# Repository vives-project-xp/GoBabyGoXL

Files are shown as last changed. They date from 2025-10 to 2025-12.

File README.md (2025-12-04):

# GOBABYGOXL (Dit is een prototype)
## Team
- [Maarten Audenaert](https://github.com/MaartenAudenaert)
- [Mauro Carlier](https://github.com/maurocarlier)
- [Danae Zutterman](https://github.com/Danaezutterman)
- [Robbe Lambrechts](https://github.com/lomopoio)
- [Thomas Demeulenaere](https://github.com/Thomas8650)
- [Jarno Bostyn](https://github.com/Jarno-max)

## De opdracht
De bedoeling is om verder te werken op het GoBabyGo-project van de vorige jaren. De doelstelling van dit project is om kinderen 
met een motorische beperking toch zelfstandig te kunnen laten voortbewegen. Dit wordt gedaan door middel van een auto waarvan 
we het gaspedaal vervangen door een knop op het stuur. De GoBabyGo was voor iets kleinere kinderen en nu is het de bedoeling dat we een 
XL-versie maken voor kinderen die te groot zijn geworden voor de vorige auto.

## Affiches

<div style="display: flex; gap: 10px;">
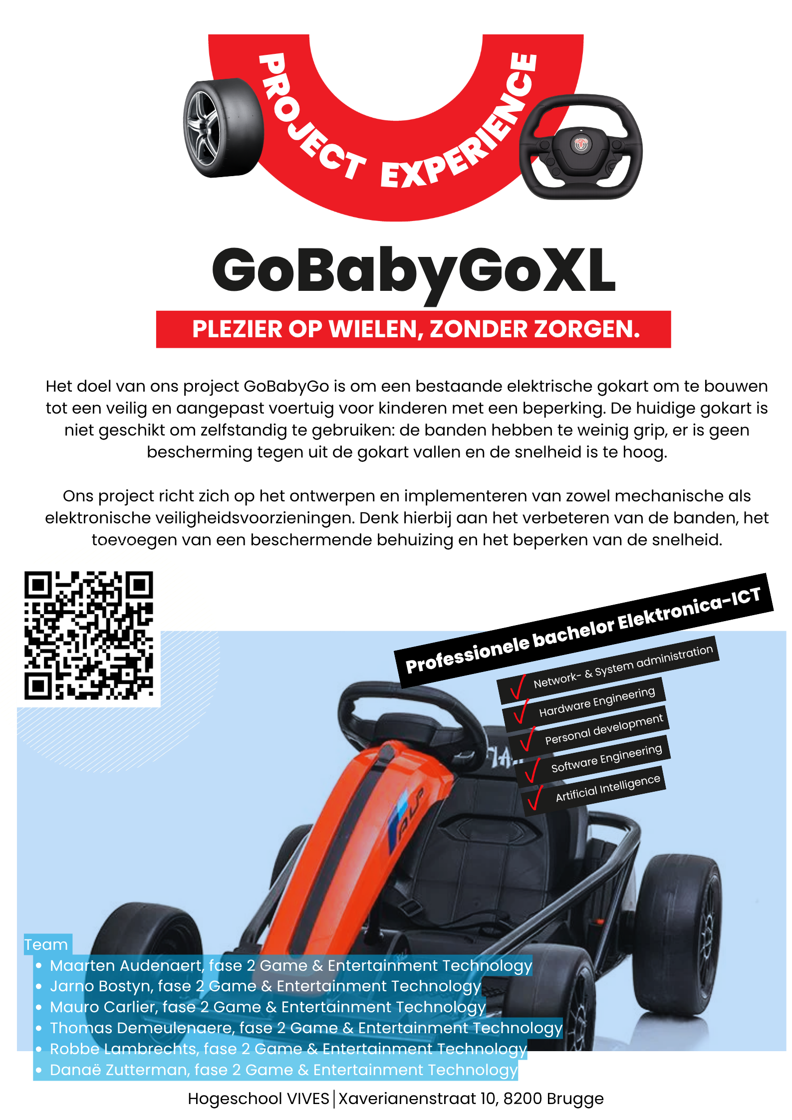
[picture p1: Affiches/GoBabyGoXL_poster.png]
   
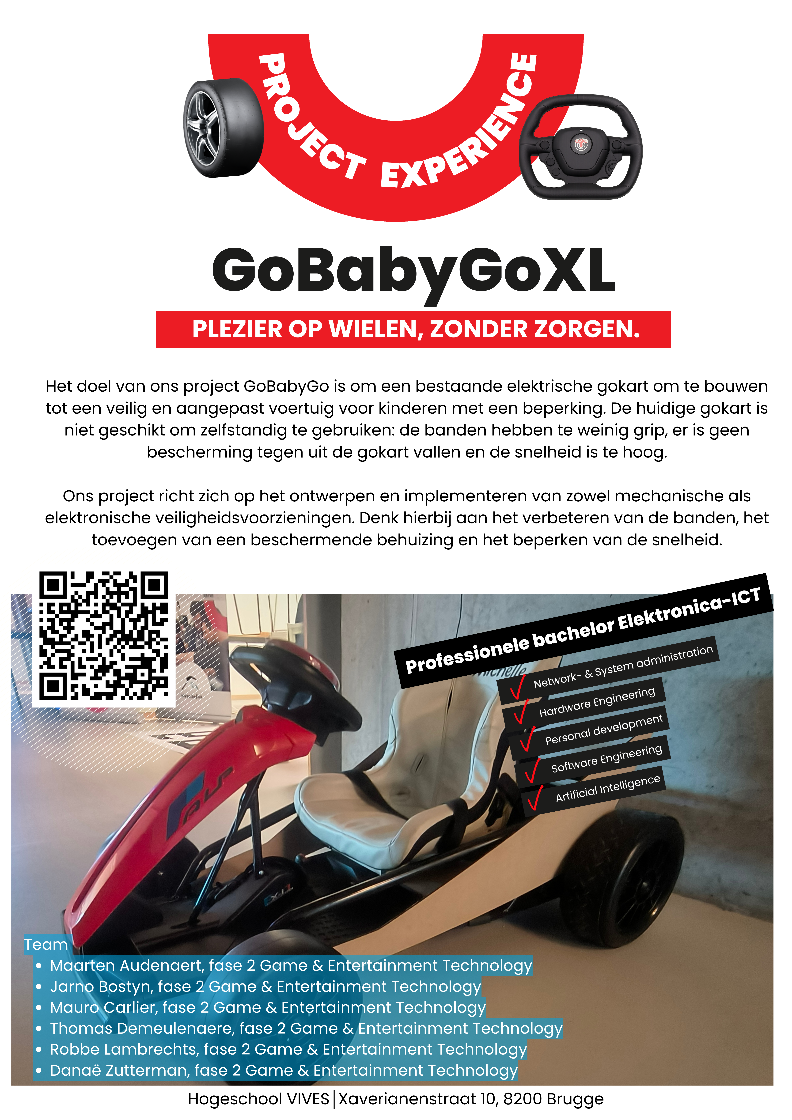
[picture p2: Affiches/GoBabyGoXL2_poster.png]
   
</div>

## Folder structuur
- [3d-prints](./3d-prints/readme.md) : Hier bevindt alles om de onderdelen te 3D-printen.
- [Affiches](./Affiches/GoBabyGoXL_poster.png ) : Hier vindt u onze poster.
- [Archief](./Archief/README.md) : Hier vindt u al onze research.
- [Gaspedaal naar knop](./Gaspedaal%20naar%20knop/README.md) : Hier bevindt alles van hoe we het  gaspedaal hebben vervangen door een knop. 
- [Grip banden](./Grip%20banden/README.md) : Hier bevindt alles hoe we de grip van de banden verbeteren.
- [Handleidingen](./Handleidingen/readme.md) : Hier vindt u de handleidingen voor het aanpassen van de auto.
- [Inriching auto](<Inrichting auto/README.md>) : Hier bevindt alles hoe we de auto veilig maken voor het kind.
- [Instagram post](./Instagram%20Post/Readme.md) : Hier vindt u onze instagram post.
- [Joystick](./Joystick/readme.md) : Hier wordt er nagedacht over de uitbreiding met een joystick.
- [Lasercutten](./Lasercutten/readme.md) : Hier bevindt alles om de onderdelen te lasercutten.

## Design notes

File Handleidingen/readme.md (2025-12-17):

# Handleiding om de auto om te bouwen
### Let op: dit is een prototype!

[**Benodigdheden om de auto om te bouwen**](#Benodigdheden)

[**Gereedschapsbenodigdheden**](#Gereedschap)

[**Handleiding om de auto om te bouwen met de knop**](#Handleiding-om-auto-om-te-bouwen-met-knop)

[**Handleiding om de auto om te bouwen met de joystick**](#Handleiding-om-auto-om-te-bouwen-met-joystick)

[**Kostprijs per auto**](#Kostprijs-per-auto)

---

## Benodigdheden 
Hier vindt u alle benodigdheden om 1 auto om te bouwen.

[**Benodigdheden knop**](#Knop)

[**Benodigdheden joystick**](#Joystick)

---
## Kostprijs per auto
[**Kostprijs**](https://github.com/vives-project-xp/GoBabyGoXL/tree/main/Handleidingen/KostprijsPerAuto)

---

### Knop

1x: [Knop Ergo](https://www.kmd.nl/producten/overige-hulpmiddelen/schakelaars/big-red)

2x: [Seconden Epoxylijm](https://www.hubo.be/nl/p/pattex-super-mix-universal-mini-epoxy-colle-bi-composant-6ml/249565/#specs)

4x: [Buizenklem 32mm](https://www.hubo.be/nl/p/astore-buisklem-32mm-polypropyleen/890700/)

6x: [Buizenklem 25mm](https://www.hubo.be/nl/p/buisklem-pp-25mm/972187/)

2x: [Buizenklem 20mm](https://www.hubo.be/nl/p/scala-buisklem-20mm-polypropyleen/994224/)

2x: [Rubber](https://www.hubo.be/nl/p/rubbermat-op-rol-traanplaat-1-5m-per-lopende-meter/131516/) (l= 86,8cm ; b=8cm)

12x: [Bouten M6 20mm](https://www.hubo.be/nl/p/mack-binnenzeskantbout-m6-20mm-verzinkt-7-stuks/208802/)

12x: [Zeskantdopmoer M6](https://www.hubo.be/nl/p/pgb-fasteners-zeskantdopmoer-din1587-m6-zwart-12-stuks/1057451/) 

1x: [Grondplaat voor stoel](https://github.com/vives-project-xp/GoBabyGoXL/tree/main/Lasercutten/Grondplaat) (lasercut)

1x: [Verhoogstuk voor stoel](https://github.com/vives-project-xp/GoBabyGoXL/blob/main/3d-prints/Helling%20stoeltje/HellingPX1%20v2.stl) (3D-print)

1x: [Velcro voor stoel](https://jbsigns.be/product/klittenband/)

1x: [Vervanging gaspedaal](https://github.com/vives-project-xp/GoBabyGoXL/blob/main/3d-prints/Gaspedaal%20plaatje/Gaspedaalv3.stl) (3D-print)

1x: [Vervanging HIGH SPEED LOW SPEED knop](https://github.com/vives-project-xp/GoBabyGoXL/blob/main/3d-prints/Dekseltje%20voor%20knop%20en%20hendel/dekseltje_sloped%20v2.stl) (3D-print)

2x: [Zijkant houten platen](https://github.com/vives-project-xp/GoBabyGoXL/tree/main/Lasercutten/Zijkant%20platen) (lasercut)

2x: [Wrapping voor zijplaten](https://www.hubo.be/nl/p/zelfklevende-folie-45cm-x-2m-mat-zwart/367781/)

1x: [Kill switch](https://rosso-parts.com/products/high-low-speed-switch)

---

### Joystick

1x: [Joystick](https://www.conrad.be/nl/p/joy-it-arcade-joystick-professional-8-invoerapparaat-geschikt-voor-arduino-banana-pi-cubieboard-pcduino-raspberry-pi-1555268.html?cq_src=google_ads&cq_cmp=21348122838&cq_term=&cq_plac=&cq_net=x&cq_plt=gp&utm_source=google&utm_medium=cpc&utm_campaign=BE+-+PMAX+-+Nonbrand+-+Zero+traffic&utm_id=21348122838&gad_source=1&gad_campaignid=21354377450&gbraid=0AAAAAD8JkRqEt0kc6sfABQWvpGkQomOKD&gclid=CjwKCAjwup3HBhAAEiwA7euZuuzKnT1HKtYVqYWcoFUZA91DAXJudML3s6RHekIYH-F_8EoZS52qvxoC-UwQAvD_BwE&refresh=true)

1x: [DC-motor](https://www.tinytronics.nl/nl/mechanica-en-actuatoren/motoren/dc-motoren/aslong-pg42-775-transmissiemotor-24v-dc-90rpm)

1x: [Dc-converter 24V --> 12V](https://www.reichelt.com/be/nl/shop/product/dc_dc-converter_12_7_v_5_a-300230?PROVID=2812)

1x: [ESP32](https://www.tinytronics.nl/nl/development-boards/microcontroller-boards/met-wi-fi/lilygo-ttgo-t-display-v1.1-esp32-met-1.14-inch-tft-display)

1x  [24V->5v USB converter module](https://www.amazon.nl/gp/product/B07JLTTZXL?smid=A3U3NV7MT8POQS&psc=1)

1x: [Driver H-brug](https://www.otronic.nl/nl/l298n-motor-driver-board-rood.html?source=googlebase&gad_source=1&gad_campaignid=19639985996&gbraid=0AAAAACZK5qu8Z-8RFgjMXGjDdSz0dZhw3&gclid=CjwKCAiA_dDIBhB6EiwAvzc1cA0ZIi9ejuDw5lKT-S1ZbPfsZyDSasSXt8XzMPAZVOmllBPeCYmQxhoCnuUQAvD_BwE)

2x: [Seconden Epoxylijm](https://www.hubo.be/nl/p/pattex-super-mix-universal-mini-epoxy-colle-bi-composant-6ml/249565/#specs)

4x: [Buizenklem 32mm](https://www.hubo.be/nl/p/astore-buisklem-32mm-polypropyleen/890700/)

6x: [Buizenklem 25mm](https://www.hubo.be/nl/p/buisklem-pp-25mm/972187/)

2x: [Buizenklem 20mm](https://www.hubo.be/nl/p/scala-buisklem-20mm-polypropyleen/994224/)

2x: [Rubber](https://www.hubo.be/nl/p/rubbermat-op-rol-traanplaat-1-5m-per-lopende-meter/131516/) (l= 86,8cm ; b=8cm)

12x: [Bouten M6 20mm](https://www.hubo.be/nl/p/mack-binnenzeskantbout-m6-20mm-verzinkt-7-stuks/208802/)

12x: [Zeskantdopmoer M6](https://www.hubo.be/nl/p/pgb-fasteners-zeskantdopmoer-din1587-m6-zwart-12-stuks/1057451/)

1x: [Grondplaat voor stoel](https://github.com/vives-project-xp/GoBabyGoXL/tree/main/Lasercutten/Grondplaat) (lasercut)

1x: [Verhoogstuk voor stoel](https://github.com/vives-project-xp/GoBabyGoXL/blob/main/3d-prints/Helling%20stoeltje/HellingPX1%20v2.stl) (3D-print)

1x: [Velcro voor stoel](https://jbsigns.be/product/klittenband/)

1x: [Vervanging gaspedaal](https://github.com/vives-project-xp/GoBabyGoXL/blob/main/3d-prints/Gaspedaal%20plaatje/Gaspedaalv3.stl) (3D-print)

1x: [Vervanging HIGH SPEED LOW SPEED knop + Voorwaarts/achterwaarts knop](https://github.com/vives-project-xp/GoBabyGoXL/blob/main/3d-prints/Dekseltje%20voor%20knop%20en%20hendel/deksel_combo.stl) (3D-print)

1x: [DC-motor houder](https://github.com/vives-project-xp/GoBabyGoXL/tree/main/3d-prints/DC-voeding%20houder) (3d-print)

1x: [Assenkoppeling](https://www.motedis.be/nl/Assen-Koppelingen-flexibel-Mot-D25L30-8-12mm)

2x: [Zijkant houten platen](https://github.com/vives-project-xp/GoBabyGoXL/tree/main/Lasercutten/Zijkant%20platen) (lasercut)

2x: [Wrapping voor zijplaten](https://www.hubo.be/nl/p/zelfklevende-folie-45cm-x-2m-mat-zwart/367781/)

1x: [Kill switch](https://rosso-parts.com/products/high-low-speed-switch)

---

## Gereedschap
- 3D printer
- Lasercutter
- Setje schroevendraaiers
- Boormachine
- Soldeerbout + accessoires
- Kniptang + universele tang
- Usb-c kabel
- Setje dopsleutels
- Dremel
- Houtlijm            
- Breekmes
- Schuifmaat/Meter
- Multimeter
- Slijpschijf
- Koperdraad/Jumper wires
- Krimpkous
- Pattex spraylijm
- Twee M4 25mm bouten
- Twee M4 50mm bouten
- Heatgun

---

## Handleiding om auto om te bouwen met knop

[**Installatie van de knop**](#Knop-installeren)

[**Bevestiging van de knop**](#Bevestiging-van-de-knop)

[**Bevestigingsplaatje voor het gaspedaal**](#Bevestigen-plaatje-van-gaspedaal)

[**Begrenzen van de snelheid**](#Snelheidsbegrenzing)

[**Bevestigensplaatje voor de High- en Low speed knop**](#Bevestigen-plaatje-van-high--en-low-speed-knop)

[**Montage van de grondplaat**](#Montage-Grondplaat)

[**Plaatsen van de stoel**](#Bevestigen-van-de-stoel)

[**Wrappen + monteren van de zijplaten**](#wrappen--monteren-van-de-zijplaten)

[**Grip voor de banden**](#Grip-banden)

[**Kill switch**](#Kill-switch)

---

### Knop installeren

Als eerste maak je de vier schroeven los zodat je het gaspedaaltje kan verwijderen.

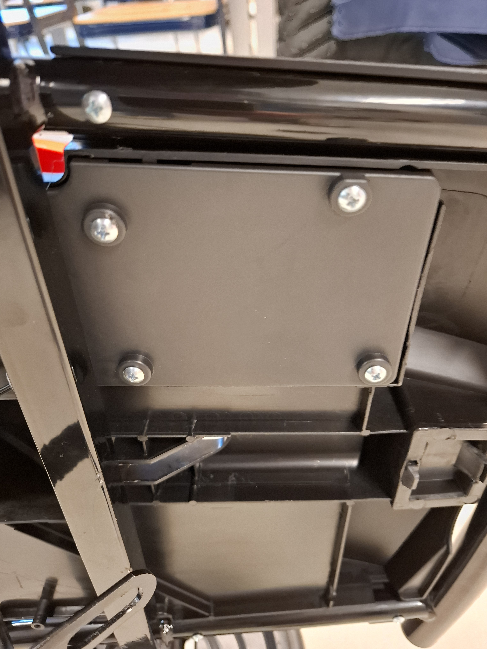
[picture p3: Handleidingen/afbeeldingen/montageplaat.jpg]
bevestigingsplaat


Het gaspedaaltje verwijder je door het met wat kracht omhoog te duwen.

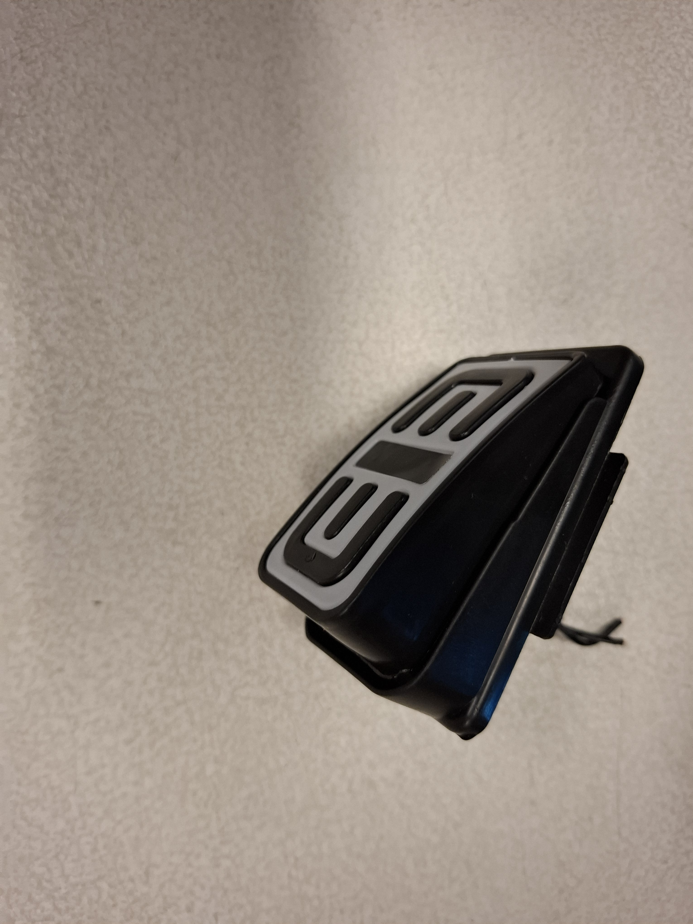
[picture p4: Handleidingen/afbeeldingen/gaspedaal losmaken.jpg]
gaspedaal


Vervolgens knip je de zwarte kabels die aan het gaspedaal vastzitten los.

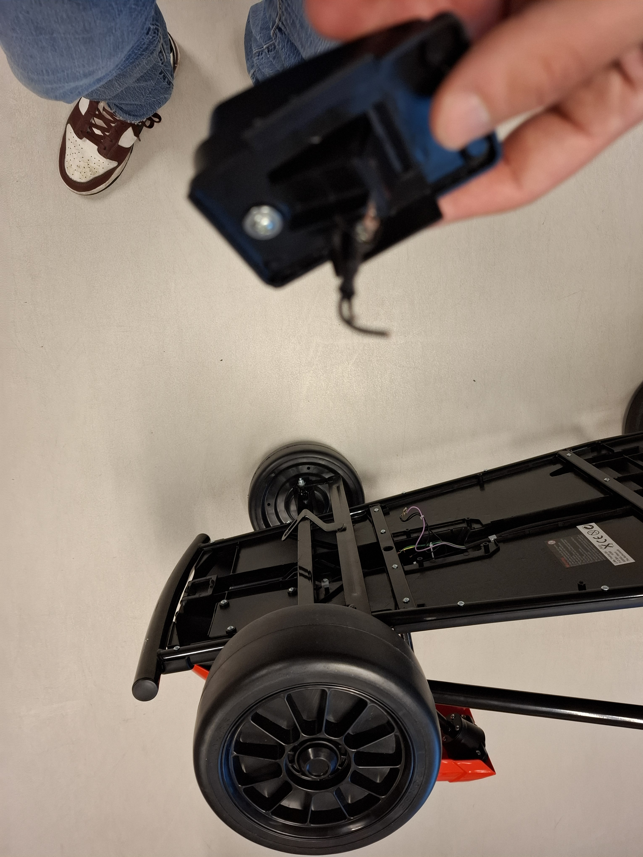
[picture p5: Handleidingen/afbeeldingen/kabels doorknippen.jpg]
kabels doorknippen


Daarna verleng je de draden van de knop en de kabels van het gaspedaal, en soldeer je deze zorgvuldig aan elkaar.

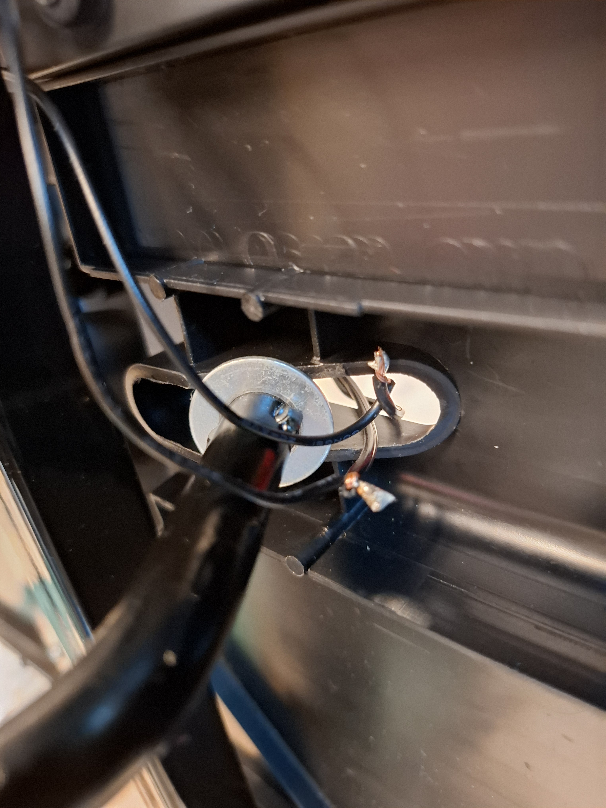
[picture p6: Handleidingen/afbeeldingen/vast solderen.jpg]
solderen


---

### Bevestiging van de knop
1) Dit is het stuur van de auto.
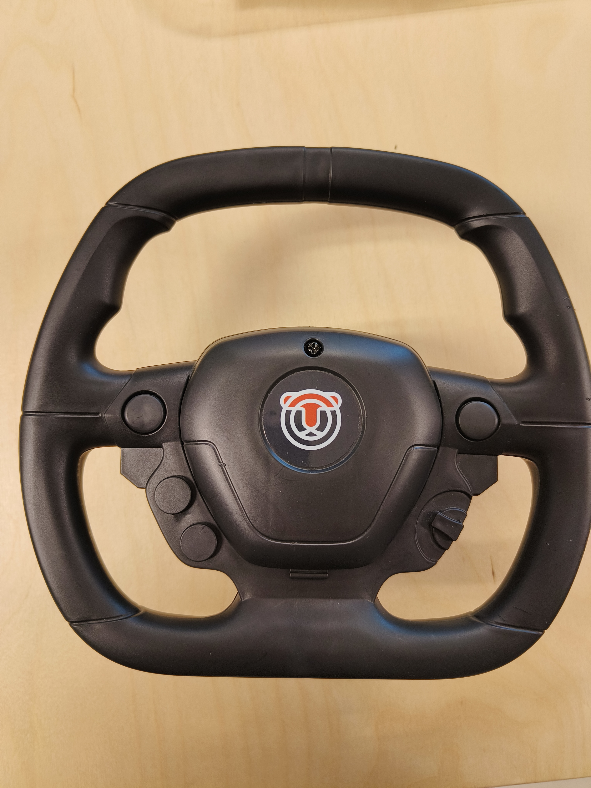
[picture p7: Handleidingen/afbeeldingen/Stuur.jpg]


2) Nu leg je de knop in het midden van het stuur, je tekent hier 1 gaatje af om de knop te bevestigen. Hierna maak je een gaatje in het stuur.
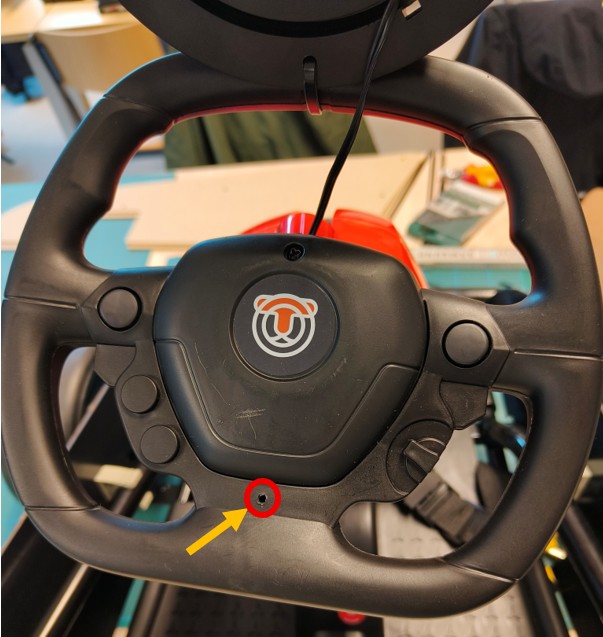
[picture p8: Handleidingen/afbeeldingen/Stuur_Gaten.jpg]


3) Nu maak je een gaatje in de knop boven en onderaan daarna plaats je de knop op het stuur, en monteer je het.
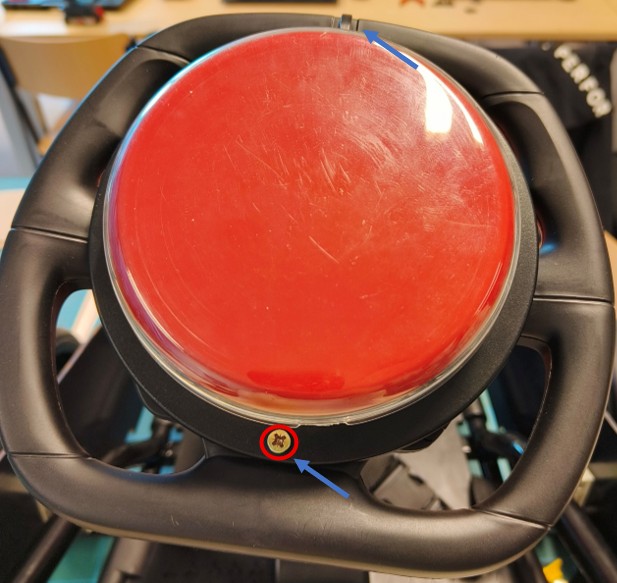
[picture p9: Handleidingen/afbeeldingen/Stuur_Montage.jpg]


---

### Bevestigen plaatje van gaspedaal
1) Eerste verwijder je het origineel gaspedaaltje.
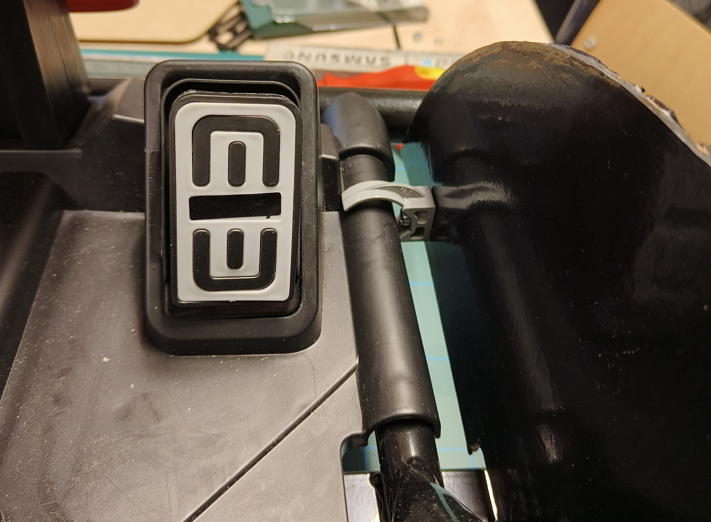
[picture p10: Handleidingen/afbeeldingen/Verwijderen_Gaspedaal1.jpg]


2) Nu heb je een lege opening.
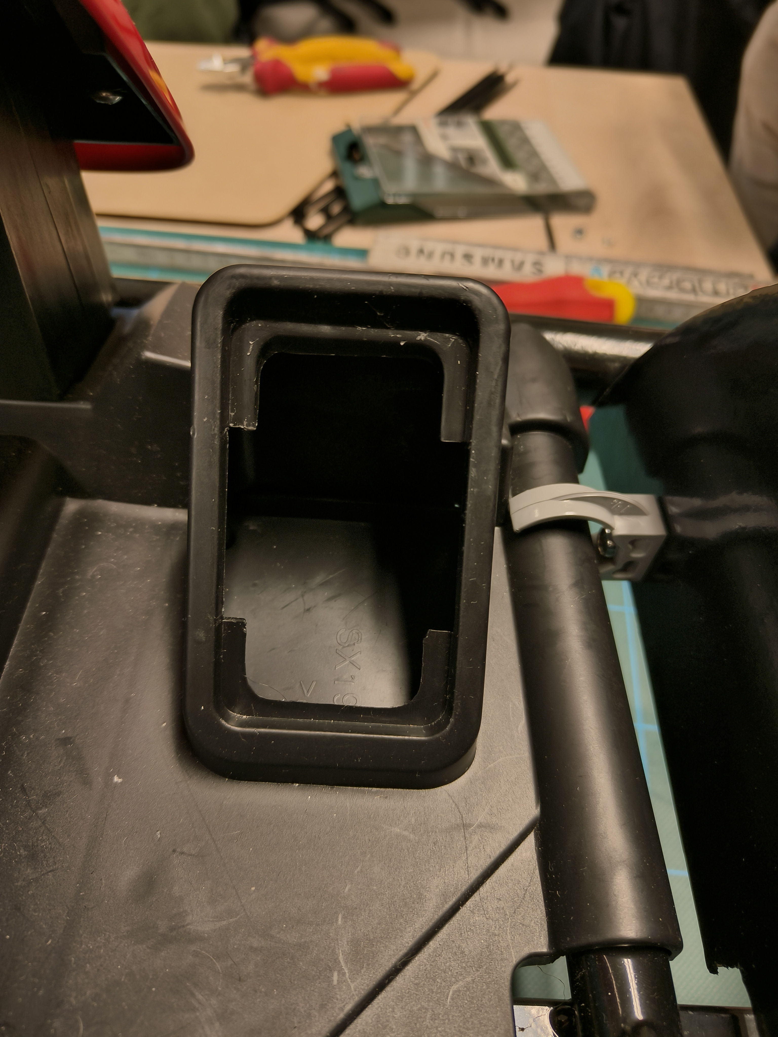
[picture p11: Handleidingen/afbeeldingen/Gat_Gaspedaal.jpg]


3) Nu plaats je het 3D geprinte gaspedaaltje, hiervoor heb je geen lijm nodig.
   
<div style="display: flex; gap: 10px;">
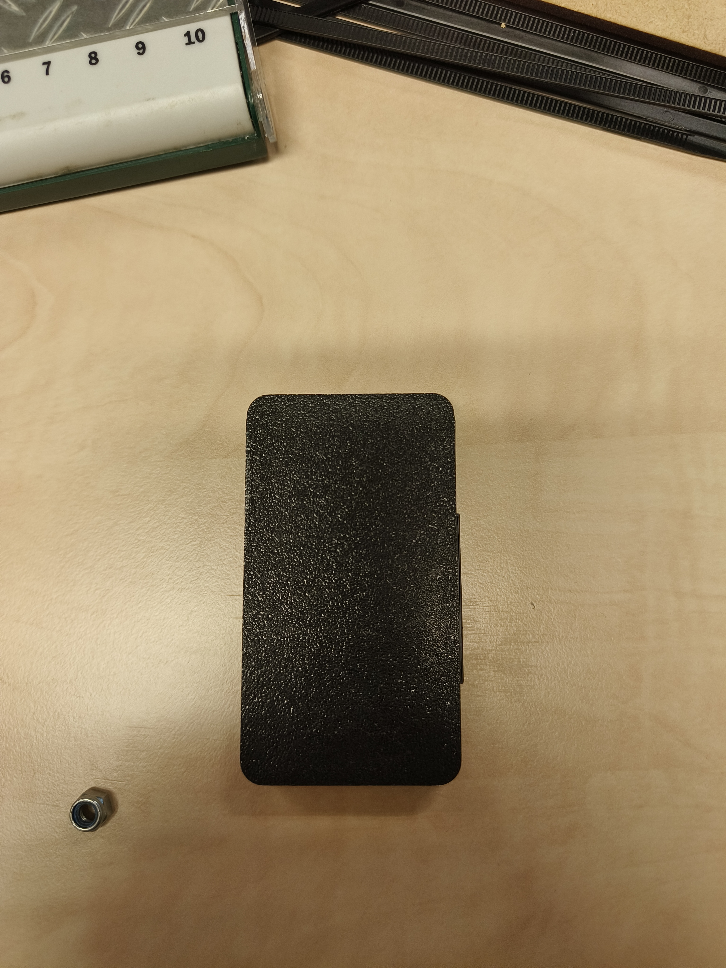
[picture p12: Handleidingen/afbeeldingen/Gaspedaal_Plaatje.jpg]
   
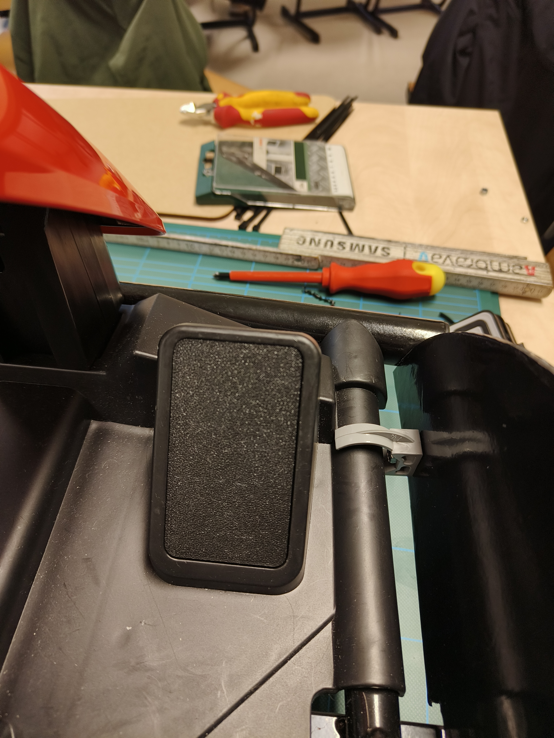
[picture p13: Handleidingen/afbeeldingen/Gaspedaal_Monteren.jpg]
   
</div>

4) Nu is het klaar.

---

### Snelheidsbegrenzing

1) Eerst open je de bescherming die aan de onderkant zit van de auto, dit doe je door de vijsjes los te maken. 
Nadat je het geopend hebt, vind je hier de schakelaar (de opening die in het blauw omcirkelt is). 
Deze schakelaar maak je los, alsook de connector van de paarse en de zwarte draad.

**Bescherming en Binnenkant**
<div style="display: flex; gap: 10px;">
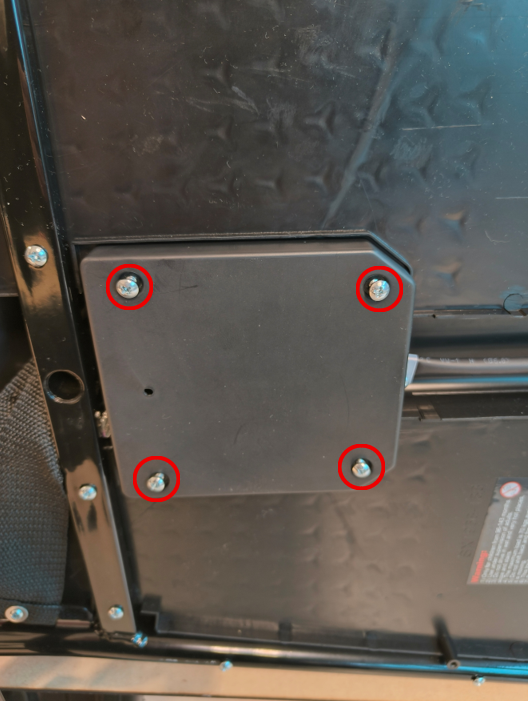
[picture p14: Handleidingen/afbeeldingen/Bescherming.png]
   
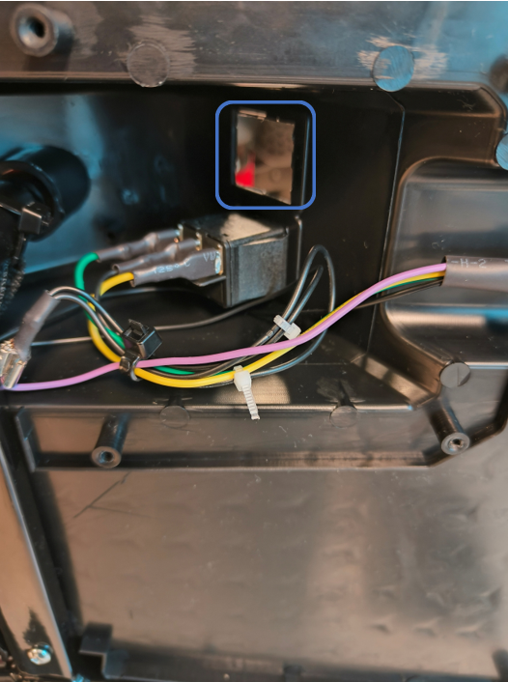
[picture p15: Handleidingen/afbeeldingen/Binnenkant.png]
   
</div>

**Schakelaar**

<div style="display: flex; gap: 10px;">
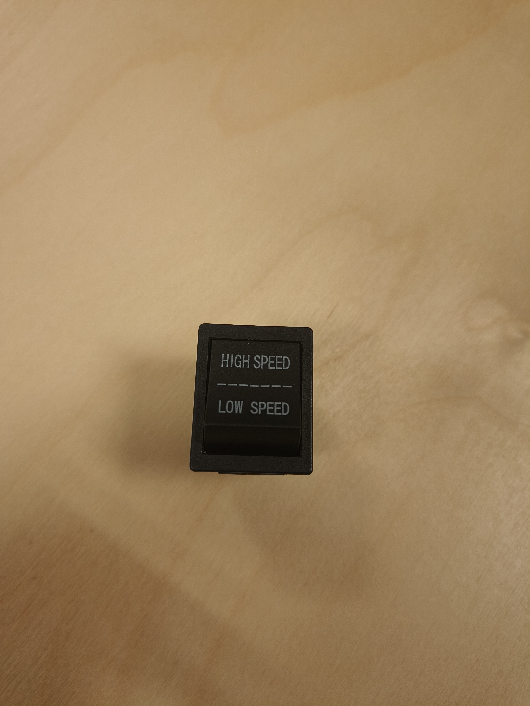
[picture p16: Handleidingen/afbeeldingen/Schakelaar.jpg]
   
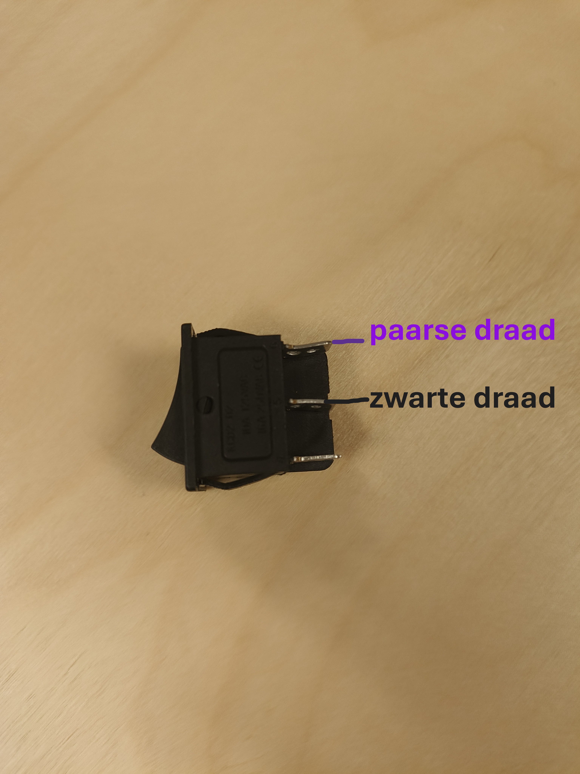
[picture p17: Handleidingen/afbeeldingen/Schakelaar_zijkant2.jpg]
   
</div>

2) Nadat je de schakelaars los hebt gekregen, alsook de paarse draad. Knip je de connector van de paarse draad door.
   Steek de paarse draad onder het metalen gedeelte zodanig dat het goed aangespannen is en hij niet snel zal los komen.
   Nu soldeer je de paarse draad aan de connector van de zwarte draad. 

**De gesoldeerde verbinding**

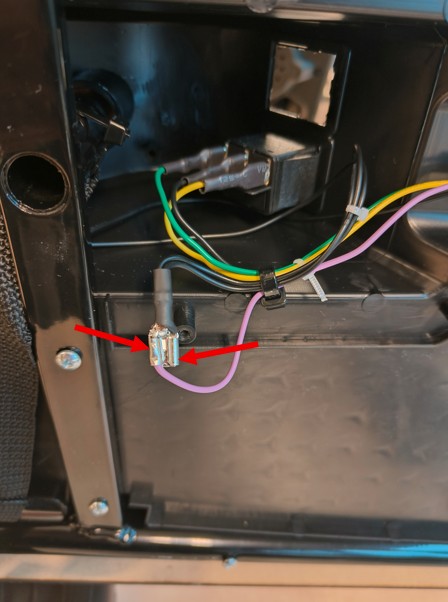
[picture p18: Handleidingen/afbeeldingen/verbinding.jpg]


3) Nu heb je de snelheid begrensd.

---

### Bevestigen plaatje van high- en low speed knop
Nadat je de snelheid begrensd hebt, plaats je het nieuwe 3D geprinte plaatje.
<div style="display: flex; gap: 10px;">
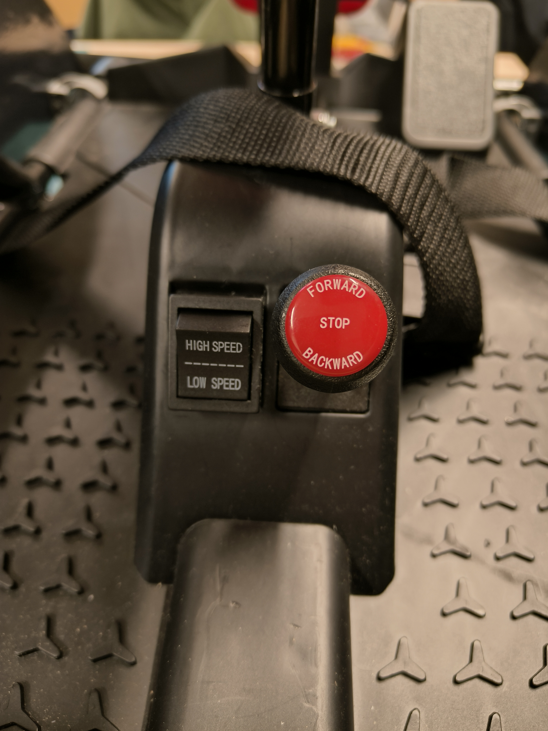
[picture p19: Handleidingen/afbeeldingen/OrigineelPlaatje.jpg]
   
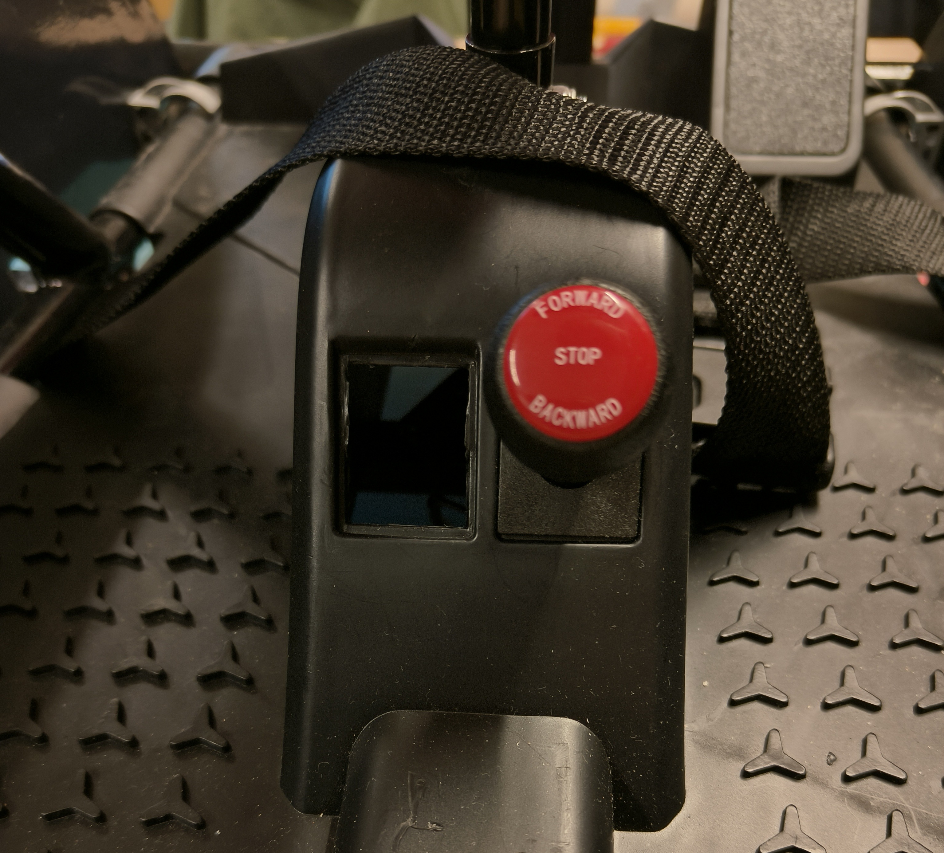
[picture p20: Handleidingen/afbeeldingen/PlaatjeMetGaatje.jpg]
   
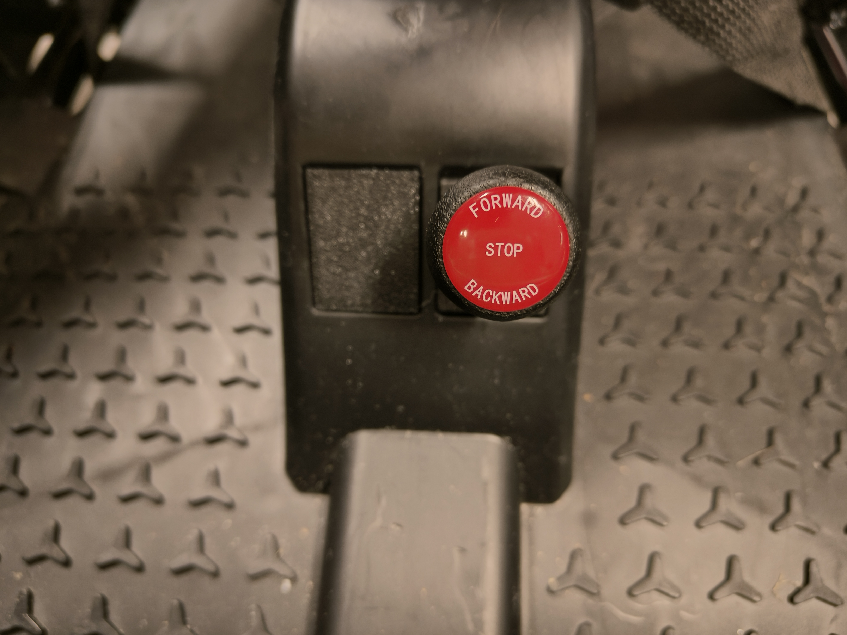
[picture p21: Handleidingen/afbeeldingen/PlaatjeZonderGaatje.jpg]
   

</div>

---

### Montage Grondplaat
1. We moeten eerst de stoel die al op de auto is aangesloten demonteren van de auto, dus alle vijzen losmaken die worden aangeduid met de rode pijlen.

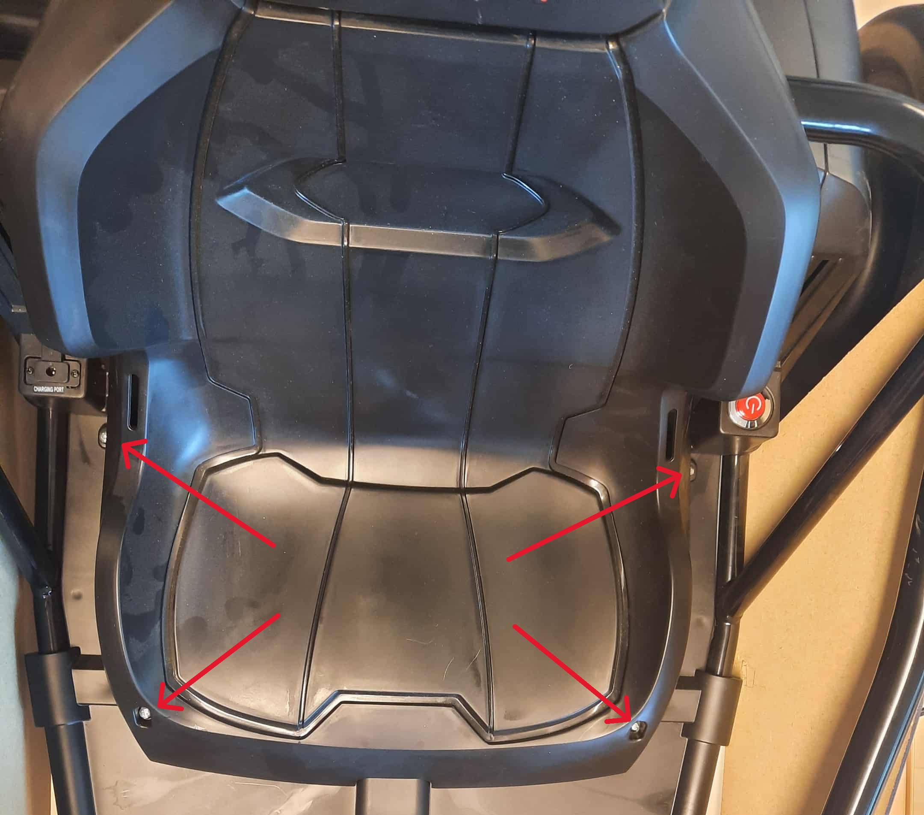
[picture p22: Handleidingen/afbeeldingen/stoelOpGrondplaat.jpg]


2. Als dit gebeurd is, monteer je nu de gelasercutte grondplaat op de auto.

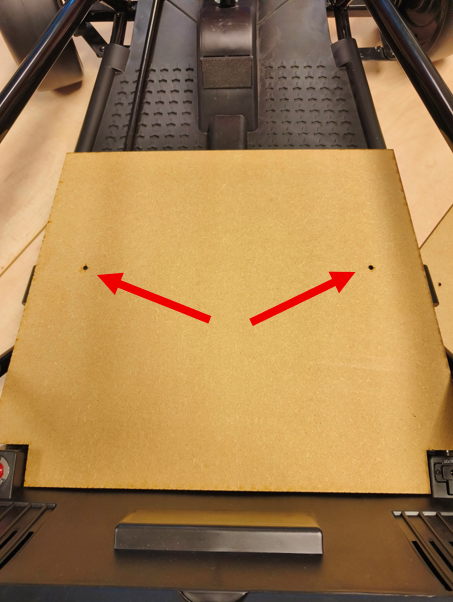
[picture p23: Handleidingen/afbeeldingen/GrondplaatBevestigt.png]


3. Zodra je dit hebt gedaan, kun je de vijzen monteren op de plaatsen waar de rode pijlen naar wijzen.

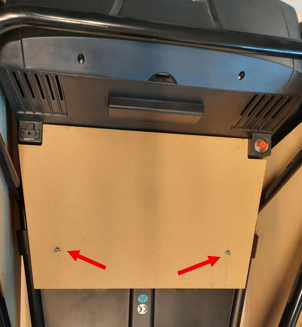
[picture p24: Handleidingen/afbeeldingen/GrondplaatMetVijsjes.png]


---

### Bevestigen van de stoel
1. Knip een stuk velcro van ongeveer 17 cm en plak dit op de ondergrond van de auto.

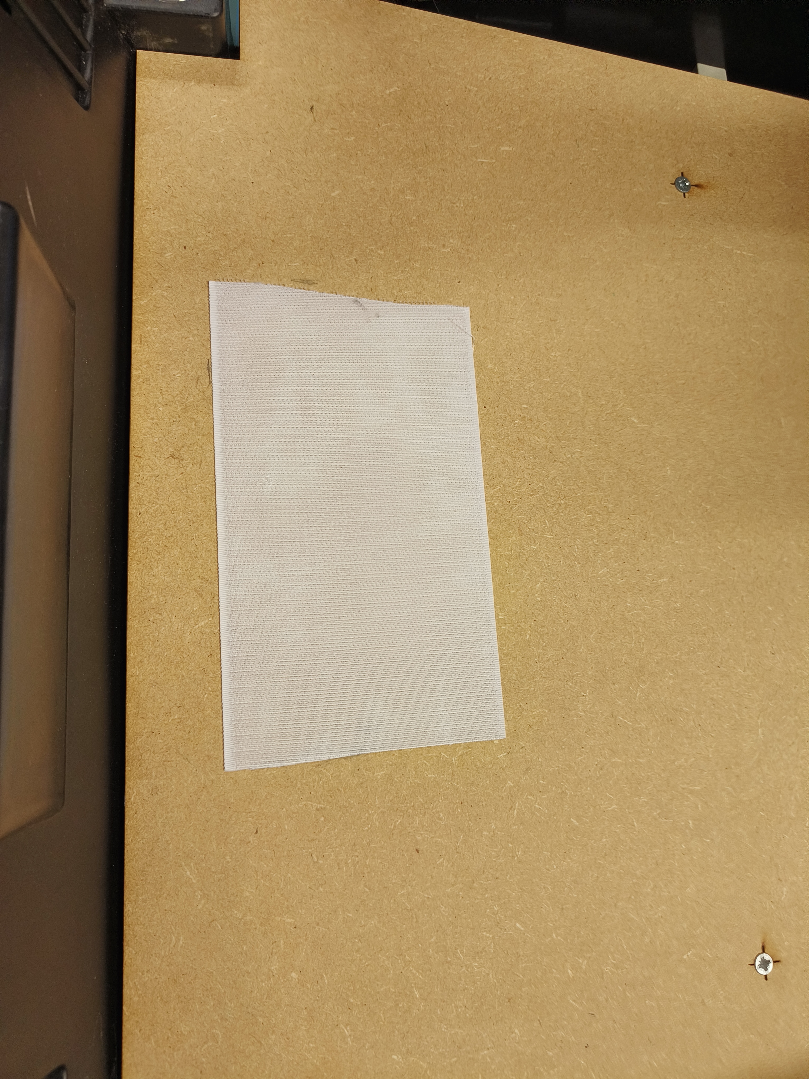
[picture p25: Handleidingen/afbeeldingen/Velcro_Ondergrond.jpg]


2. Knip nog een stuk velcro met ongeveer dezelfde lengte als die van de ondergrond en plak deze op de stoel.
   
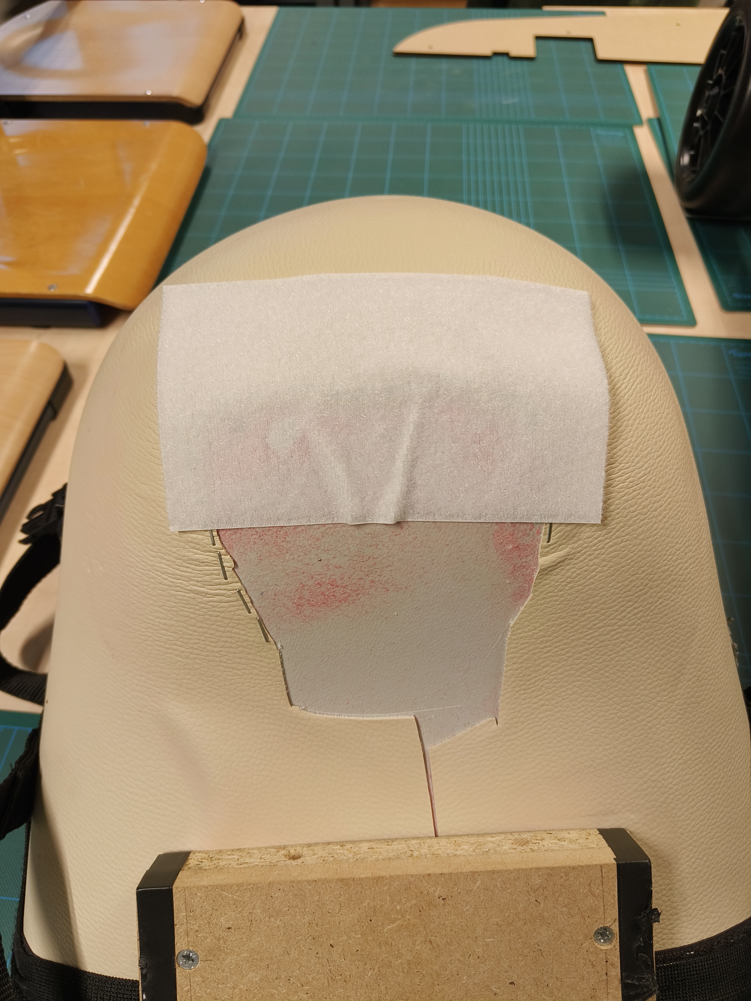
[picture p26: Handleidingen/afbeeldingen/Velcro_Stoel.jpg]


3. Zet de stoel op de ondergrond, nu is de stoel gemonteerd.



---

### Wrappen & monteren van de zijplaten

Je neemt de gelasercutte platen en je legt de wrapfolie erover, deze folie lijm je met houtlijm. Hierna snij je overschot van de folie weg met een breekmes.



Daarna plaats je de juiste klemmen op de juiste plaats, zie afbeelding hieronder.



Hierna zet je de klemmen vast met de M6 bouten.



Nu is het klaar.



---

### Grip banden
1. Je snijdt de rubbermat op maat

   
   
2. De binnenzijde van de rubbermat en de buitenzijde van de banden werden eerst **schoon gemaakt**.

     

     
3. Vervolgens werd **Pattex spraylijm** en **Epoxy lijm** aangebracht rondom **het plastic ** van de band.  
4. De rubbermat werd zorgvuldig om de banden gewikkeld en stevig aangedrukt via een spanband.  
5. Na het **uitharden van de lijm** was de rubberlaag stevig bevestigd.

   
   
---

### Kill switch

1. Je maakt een gat voor de kill switch in de kap van de batterij.

   
   
2. Je soldeert de kabels aan de kill switch.

   

   

3. Dan knip je de rode kabel door die naar de knop gaat en plaats je daar tussen de kill switch.

   

4. Daarachter monteer je de knop in de kap van de batterij.

   

5. Nu verbindt je de kabels van de switch met de kabels die je hebt doorgeknipt.

   

6. Als laatste vijs je de kap vast en heb je het eindresultaat.

   

---

## Handleiding om auto om te bouwen met joystick

[**Bevestigingsplaatje voor het gaspedaal**](#Bevestigen-plaatje-van-gaspedaal)

[**Begrenzen van de snelheid**](#Snelheidsbegrenzing)

[**Plaatje voor HIGH/LOW speed knop + voorwaarts/achterwaarts knop**](#bevestigen-plaatje-van-high--en-low-speed-knop--voorwaartsachterwaarts-knop)

[**Montage van de grondplaat**](#Montage-Grondplaat)

[**Plaatsen van de stoel**](#Bevestigen-van-de-stoel)

[**Wrappen + monteren van de zijplaten**](#wrappen--monteren-van-de-zijplaten)

[**Grip voor de banden**](#Grip-banden)

[**Kill switch**](#Kill-switch)

[**Maken van het stuurmechanisme met de DC-Motor**](Monteren-van-de-DC--houder)

[**Voeding DC-motor en esp**](#voeding-DC-motor-en-esp-1)

[**Installatie van de joystick**](#Joystick-installeren)

[**Bevestiging van de joystick**](#Bevestiging-van-de-joystick)

[**vouruitacheruit-op-joystick**](#vouruitacheruit-op-joystick)

[**Code inladen in esp**](#code-inladen-in-esp)

--- 

### Bevestigen plaatje van gaspedaal

1) Eerst verwijder je het origineel gaspedaaltje.


2) Nu heb je een lege opening.


3) Nu plaats je het 3D geprinte gaspedaaltje, hiervoor heb je geen lijm nodig.
<div style="display: flex; gap: 10px;">
   
   
</div>
4) Nu is het klaar

---

### Snelheidsbegrenzing

1) Eerst open je de bescherming die aan de onderkant zit van de auto, dit doe je door de vijsjes los te maken. 
Nadat je het geopend hebt, vind je hier de schakelaar (de opening die in het blauw omcirkelt is). 
Deze schakelaar maak je los, alsook de connector van de paarse en de zwarte draad.

**Bescherming en Binnenkant**
<div style="display: flex; gap: 10px;">
   
   
</div>

**Schakelaar**

<div style="display: flex; gap: 10px;">
   
   
</div>

2) Nadat je de schakelaars los hebt gekregen, alsook de paarse draad. Knip je de connector van de paarse draad door.
   Steek de paarse draad onder het metalen gedeelte zodanig dat het goed aangespannen is en hij niet snel zal los komen.
   Nu soldeer je de paarse draad aan de connector van de zwarte draad. 

**De gesoldeerde verbinding**



3) Nu heb je de snelheid begrenst.

---

### Bevestigen plaatje van high- en low speed knop + Voorwaarts/Achterwaarts knop
Voor dit onderdeel heb je het 3D geprinte plaatje nodig genaamd "Vervanging HIGH SPEED LOW SPEED knop + Voorwaarts/achterwaarts knop". 



Nu plaats je het plaatje over het gaatje.



Nu is het klaar.

---

### Montage grondplaat
1. We moeten eerst de stoel die al op de auto is aangesloten demonteren van de auto, dus alle vijzen losmaken die worden aangeduid met de rode pijlen.



2. Als dit gebeurd is, monteer je nu de gelasercutte grondplaat op de auto.



3. Zodra je dit hebt gedaan, kun je de vijzen monteren op de plaatsen waar de rode pijlen naar wijzen.



---

### Bevestigen van de stoel
1) Knip een stuk velcro van ongeveer 17 cm en plak dit op de ondergrond van de auto.



2) Knip nog een stuk velcro met ongeveer dezelfde lengte als die van de ondergrond en plak deze op de stoel.
   


3) Zet de stoel op de ondergrond, nu is de stoel gemonteerd.



---

### Wrappen & monteren van de zijplaten

Je neemt de gelasercutte platen en je legt de wrapfolie erover, deze folie lijm je met houtlijm. Hierna snij je overschot van de folie weg met een breekmes.



Daarna plaats je de juiste klemmen op de juiste plaats, zie afbeelding hieronder.



Hierna zet je de klemmen vast met de M6 bouten.



Nu is het klaar.



---

### Grip banden
1. Je snijdt de rubbermat op maat.

   
   
2. De binnenzijde van de rubbermat en de buitenzijde van de banden werden eerst schoongemaakt.

     

     
3. Vervolgens werd Pattex spraylijm en Epoxy lijm aangebracht rondom het plastiek van de band.  
4. De rubbermat werd zorgvuldig om de banden gewikkeld en stevig aangedrukt via een spanband.  
5. Na het uitharden van de lijm was de rubberlaag stevig bevestigd.

   
   
---

### Kill switch

1. Je maakt een gat voor de kill switch in de kap van de batterij.

   
   
2. Je soldeert de kabels aan de kill switch.

   

   

3. Dan knip je de rode kabel door die naar de knop gaat en plaats je daar tussen de kill switch.

   

4. Daarachter monteer je de knop in de kap van de batterij.

   

5. Nu verbindt je de kabels van de switch met de kabels die je hebt doorgeknipt.

   

6. Als laatste vijs je de kap vast en heb je het eindresultaat.

   

### Maken van het stuurmechanisme met de DC-Motor
We kozen de locatie boven het gat waar normaal de stalen stuurstang doorheen loopt. Dit is de mechanische verbinding die oorspronkelijk voor de besturing zorgde.
Op deze plek is voldoende ruimte om de DC-Motor in dezelfde hoek als de stang te plaatsen, wat dus zorgt voor een optimale krachtsoverdracht op het stuurmechanisme.

 Plaats van de DC-Motor op de auto

Hier zie je op de foto het gat (waar de stang doorheen loopt) waarop we de DC-motor bovenop zullen bevestigen. 

Wanneer de DC-motor eenmaal op de juiste positie is bevestigd via de printplaat, moet de motoras nog gekoppeld worden aan het stuurmechanisme. We maken hiervoor gebruik van de originele stang, omdat het uiteinde daarvan perfect past in de onderzijde van het stuurmechanisme.



Voor de verbinding tussen de motoras en de stang gebruiken we een flexibele assenkoppeling (Assen Koppeling flexibel Mot D25L30, 8/12 mm). Deze koppeling sluit aan de ene kant perfect aan op de 8 mm motoras en aan de andere kant op de 12 mm stang. Beide zijden kunnen stevig worden vastgezet met inbusbouten, waarvoor een 2 mm en 2,5 mm inbussleutel nodig is.

<p align="left">


<p>

De stang moest natuurlijk nog worden ingekort, omdat deze in de nieuwe configuratie veel minder lang hoeft te zijn. De stang is vanaf de bovenkant … ingekort. Hieronder zie je het complete eindresultaat van het aangepaste stuurmechanisme dat nu door de DC-motor wordt aangedreven.

### Voeding DC-motor en esp

1. Het eerste wat je moet doen is de bruine en de rode kabel doorsnijden bij de witte connector.

   

2. Wanneer dit gedaan is, moeten de kabels worden doorgeknipt en gestript. Vervolgens heb je twee extra kabels van ongeveer 10 cm nodig, die je    toevoegt aan de rode en bruine draad. Let er daarbij op dat de extra kabels dezelfde dikte hebben als de originele rode en bruine kabel, zodat ze de stroom veilig kunnen dragen.

3. Soldeer vervolgens de drie kabels aan elkaar en schuif er een krimpkous overheen. Vergeet niet om de krimpkous al vóór het solderen over de kabel te schuiven, anders kun je hem er nadien niet meer over krijgen.

   
   
4. Dan kun je de krimpkous mooi over de soldering doen en hem smelten met je soldeerbout                                                                of aansteker zodat deze mooi vast zit rond de soldering.
   
   

5. Nu kunnen we de aangekochte DC-converter (24 V → 12 V) aansluiten om zowel de motor als de ESP van voeding te voorzien. Dit doen we door de          bruine kabel aan te sluiten op de negatieve ingang (input −) en de rode kabel op de positieve ingang (input -).
    

6. Vervolgens moeten we de kabels aansluiten om zowel de H-brug als de ESP (via de USB-converter) van voeding te voorzien. Hiervoor sluiten we twee  kabels aan op de negatieve uitgang (output −) en twee kabels op de positieve uitgang (output +). Daarna trekken we deze kabels door het gat, samen met de kabels die er eerder al doorheen zijn geleid. 




7. Dan kun je de kabels voor de H-brug voeding aansluiten dit staat allemaal uitgelegd in [aanluitschema](/Joystick/uitleg_eleketrisch_schema.md)

8. Dan kunnen we beginnen met de de draden voor de Dc-motor aan te sluiten de kabels moeten 50 cm zijn en soldeer je aan aan de pinnen van de Dc-motor. Deze kabels moeten aan de H-brug dan ook maar zie puntje hierboven voor het schema.
   

9. We hebben nu nog twee kabels over voor de USB-converter om de ESP van voeding te voorzien. Zorg ervoor dat je de positieve kabel (+) correct aan de positieve aansluiting soldeert en de negatieve kabel (−) aan de negatieve aansluiting. Zodra dit gelukt is, hoef je enkel nog de USB-C-kabel aan te sluiten op de ESP en is alles klaar voor gebruik.

--- 

### Joystick installeren
1. De lengte van de draden voor de joystick is 76 cm. In totaal heb je er acht nodig: vier draden voor de datakabels die worden aangesloten op de pinnen van de ESP, en vier draden die worden aangesloten op de GND van de ESP.

2. Dan moeten deze kabels doorgetrokken worden naar onderaan voor de aanluiting op de esp namelijk op deze pinnen. Voor de kabels mooi weg te steken plakken we ze vast aan het rode stuk en steek je ze in het van je sturing 
[aanluitschema](/Joystick/uitleg_eleketrisch_schema.md)




---

### Bevestiging van de joystick

Om te beginnen halen we het origineel stuur er af, dit doen we door de vijzen er uit te halen.



Voor je eigen gemak haal je best ook het rode stuk eruit, dit doe je door gewoon van onder er aan te trekken.



Eerste maak je de joystick vast met de 2 M4 25mm bouten, je haalt ook de rode bol er af voor het middengat.



Nu kan je de box dichtmaken dit doe je door de bovenkant op de box te zetten en de 2 M4 50mm bouten in de voorziene gaten te steken. 



Nu verwijder je een stuk van het rode gedeelte zodat de box van de joystick erop past.



Eenmaal dit gebeurd is kan je de box monteren op het stuk waar het origineel stuur stond.

<div style="display: flex; gap: 10px;">
   
   

Dan kun je de vijzen opnieuw hergebruiken om de box terug vast te maken, je hebt ook nog een 3D geprinte stukje nodig genaamd "montage joy2.stl" om de box goed te monteren.



Nu kan je de box goed monteren zodat deze goed vast staat. Hierna kan je terug het rode stukje terug monteren.


Nu is het klaar.

### Vouruit/acheruit op joystick 
1. Om de vooruit en acheruit ook op de joystick moeten te zetten hebben we eerst de orignele joystick verwijderd dit word beschreven bij: Bevestigen plaatje van high- en low speed knop + Voorwaarts/Achterwaarts knop 
2. Als die joystick hebt verwijderd heb je 3 kables over namelijk een gele,groen en een zwarte.Deze sluit je aan volgens dit schema  
[aanluitschema](/Joystick/uitleg_eleketrisch_schema.md)


Dit wat de laatste stap voor het solderen en dan kun je op de foto zien hoe we alles hebben weggestoken


### Code inladen in esp
1. De code die we gebruiken is namelijk deze : [code](/Joystick/Code's/test_dc_limit2.ino)
Deze code is wel nog niet volledig af omdat we deze nog niet volledig hebben kunnen testen

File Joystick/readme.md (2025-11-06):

# Joystick

## Doelstelling
Het doel hiervan is dat we het originele stuur met de drukknop aanpassen naar een joystick die eigenlijk alles doet zowel vooruit als achteruit rijden (dit wordt gedaan door de vooruit- achteruitstick te verwisselen met de joystick) en ook als we de joystick naar links of rechts bewegen dat de auto de gewenste richting opgaat. 

## Ideeën
Het idee is om een DC-Motor in plaats van het stuur te plaatsen die naar recht en links kan bewegen. Deze motor zou worden aangestuurd met een esp32 die dan zo ook aan de joystick hangt. Als de joystick een signaal dan aan de esp32 geeft zal deze dan reageren op het gewenste signaal. 

## mogelijk nodig materiaal
### Esp32
Zouden we gebruiken als microcontroller om alles aan te sturen. 
esp32

### DC-Motor
Zouden we gebruiken om de originele stuuras die nu aan het stuur vasthangt te vervangen zodat we ook naar links en rechts kunnen sturen. We weten wel nog niet hoe sterk we onze DC-Motor moeten laten draaien dus dat moeten we nog eens uitzoeken. 

### Voeding
Misschien dat we hiervoor kijken voor een aparte powerbank voor de esp en de DC-Motor oftewel taken we af van de batterij zelf. Het hangt vooral ook af van hoeveel spanning en stroom de DC-Motor zal trekken.

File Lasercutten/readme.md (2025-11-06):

# Lasercutten
  Deze map bevat alle onderdelen voor de verschillende stukken te lasercutten zoals de grondplaat van de stoel en de zijplaten van de auto.

## Onderdelen
- [Grondplaat](./Grondplaat) : Hier vindt u de dxf-file om de grondplaat te lasercutten.
- [Zijkant platen](./Zijkant%20platen) : Hier vindt u de dxf-file om de zijplaaten te lasercutten.

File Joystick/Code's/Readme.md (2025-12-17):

# Joystick 

## joystick_uitlezen

Om de waarden van de joystick in te lezen, hebben we een code geschreven die de toestand van de schakelaars van de joystick doorstuurt naar de ESP32. Deze toestanden worden vervolgens weergegeven in de Serial Monitor. De volgende stap is om de besturing aan te passen, zodat we met de joystick vooruit en achteruit kunnen rijden, en naar links en rechts kunnen sturen.

filmpje_joystick

## voor-achteruit_code
In deze code hebben we de vooruit/achteruitfunctie, die oorspronkelijk door de joystick werd aangestuurd, vervangen door de ESP32. De ESP32 beslist nu zelf of de auto vooruit of achteruit rijdt. Dit gebeurt via twee pinnen die hoog worden gezet; afhankelijk van welke pin hoog staat, zal de auto vooruit of achteruit bewegen.

## DcMotor testen_code
In deze code hebben we de DC-motor getest met een eenvoudig programma waarin de motor via de ESP en de H-brug eerst enkele seconden naar rechts draait en daarna een paar keer naar links.

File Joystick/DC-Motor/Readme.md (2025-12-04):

# DC-Motor

We hebben ervoor gekozen om twee DC-Motoren aan te kopen, omdat we nog niet precies weten hoe krachtig de DC-Motor moet zijn. Hieronder staan de twee aangekochte DC-Motoren met hun specificaties.

## DC-Motor 1

Dit is de eerste DC-Motor dat we hebben gekozen namelijk de : Aslong JGB37-3530

 

### Specificaties
- DC-Motor
- Voeding: 12V
- Stroom: 200mA
- Max snelheid : 20rpm
- Max houdkoppel: 7,3 N.m

## DC-Motor 2 
Dit is de tweede DC-Motor dat we hebben gekozen namelijk de :Aslong PG42-775

DC-Motor

### Specificaties
- DC-Motor
- Voeding: 24V
- Stroom: 500mA
- Max snelheid : 88rpm
- Max houdkoppel: 12 N.m

Voor de montage van de joystick hebben we volgende dingen nodig
2 korte bouten
2 lange bouten 
4 moertjes
de 3de print joystick box
de 3de print joystick montage
en de joystick zelf

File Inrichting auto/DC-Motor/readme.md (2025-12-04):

# Stuurmechanisme met DC-Motor

Voor de auto met joystickbesturing gebruiken we een **DC-Motor** om de **voorwielen te laten draaien**.  
Om een betrouwbare en precieze werking te garanderen, moest deze motor **stevig en netjes bevestigd** worden op het chassis van de auto.  
Hieronder volgt een overzicht van het volledige ontwerpproces, van plaatsbepaling tot het 3D-ontwerp van de houder.

---

### Plaatsbepaling op de auto

Eerst hebben we onderzocht **waar op de auto** de DC-Motor het best gemonteerd kon worden.  
We kozen de locatie **boven het gat waar normaal de stalen stuurstang** doorheen loopt. Dit is de mechanische verbinding die oorspronkelijk voor de besturing zorgde.  
Op deze plek is **voldoende ruimte** om de DC-Motor **in dezelfde hoek** als de stang te plaatsen, wat dus zorgt voor een optimale krachtsoverdracht op het stuurmechanisme.

<p align="center">
  Plaats van de DC-Motor op de auto
</p>
Hier zie je op de foto het gat (waar de stang doorheen loopt) waarop we de DC-motor bovenop zullen bevestigen.

### Opmeten en voorbereiden

Daarna hebben we de gekozen positie **uitgemeten** en op papier overgezet.  
Zo konden we bepalen **hoe groot de DC-Motor houder mocht zijn** en controleren of er **voldoende plaats** was in de omgeving van het stuurmechanisme.  
Bij deze stap hielden we rekening met de **afmetingen van de DC-Motor zelf** en eventuele ruimte voor bevestigingsvijzen.

<p align="center">
  Papieren schets van de DC-Motor positie
  Afmetingen van de DC-Motor op schets
</p>

### Ontwerp in Fusion 360

Om de motor te kunnen bevesitgen op de auto hebben we gekozen om hier voor een **3D-ontwerp** te maken in **Fusion 360**. 

Het model is zo ontworpen dat de **DC-Motor perfect in de houder past** en via 4 montage gaten (M4) vanonder kan vast gemaakt worden aan de houder zelf. Dit voorkomt dat de motor beweegt tijdens het gebruik.  
Daarnaast bevat het ontwerp nog 3 **montagegaten van 4 mm diameter**, waarmee de houder met bouten **stevig op de auto kan worden bevestigd**.

Het ontwerp is zo gemaakt dat de as exact in lijn staat met de originele stang, dus ook onder dezelfde hoek. Dit is bewust gedaan, omdat we de originele stang opnieuw gaan gebruiken.

<p align="center">
  DC-Motor houder - voorkant
  DC-Motor houder - achterkant
  DC-Motor houder - onderkant
</p>

### Verbinding met stuurmechanisme
Wanneer de DC-motor eenmaal op de juiste positie is bevestigd via de printplaat, moet de motoras nog gekoppeld worden aan het stuurmechanisme. We maken hiervoor gebruik van de originele stang, omdat het uiteinde daarvan perfect past in de onderzijde van het stuurmechanisme. 

DC-Motor houder - voorkant

Voor de verbinding tussen de motoras en de stang gebruiken we een flexibele assenkoppeling (Assen Koppeling flexibel Mot D25L30, 8/12 mm). Deze koppeling sluit aan de ene kant perfect aan op de 8 mm motoras en aan de andere kant op de 12 mm stang. Beide zijden kunnen stevig worden vastgezet met inbusbouten, waarvoor een 2 mm en 2,5 mm inbussleutel nodig is. 

<p align="center">
DC-Motor houder - voorkant
DC-Motor houder - voorkant
<p>

De stang moest natuurlijk nog worden ingekort, omdat deze in de nieuwe configuratie veel minder lang hoeft te zijn. De stang is vanaf de bovenkant … ingekort. Hieronder zie je het complete eindresultaat van het aangepaste stuurmechanisme dat nu door de DC-motor wordt aangedreven.

### Resultaat
...

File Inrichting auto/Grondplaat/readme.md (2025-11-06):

# Grondplaat

Hier vind je alle informatie over de **grondplaat** die we hebben ontworpen en gemaakt.  
Op deze plaat kan de stoel worden bevestigd met behulp van **velcrostrips**.

## Stap 1: Stoel ontkoppelen van de auto

Eerst hebben we de stoel losgekoppeld van de auto om een correcte basis te hebben voor de grondplaat.

Stoel ontkoppelen

## Stap 2: Schets

We maakten een schets op papier van hoe de grondplaat eruit moest zien.  
Hierbij noteerden we meteen de juiste afmetingen om later nauwkeurig te kunnen werken.

Schets van de grondplaat

**Deze afmetingen zijn nog niet juist en worden nog aangepast in latere versies!!**

## Stap 3: Ontwerp in Fusion 360

Op basis van de papieren schets maakten we een digitale tekening in **Fusion 360**.  
Van deze tekening exporteerden we een **DXF-bestand** (terug te vinden in de "Lasercutten" map), zodat de grondplaat later kon worden uitgesneden met de **lasercutter**.

Fusion 360 ontwerp
2D-model

## Stap 4: Laser cutten en afwerking

Voor de grondplaat gebruikten we een **MDF-plaat van 6 mm dikte**.  
Dit materiaal is stevig genoeg om het gewicht van een kind te dragen.

Na het lasercutten hebben we de plaat met **twee vijzen** (diameter 5 mm) aan de auto bevestigd.

Tot slot hebben we **velcrostrips** op de grondplaat aangebracht, zodat de stoel eenvoudig kan worden vastgemaakt en indien nodig weer aangepast. Op deze manier kunnen er ook verschillende stoelen snel en eenvoudig bevestigd worden op de auto.




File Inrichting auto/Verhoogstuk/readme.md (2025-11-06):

# Verhoging stoeltje

Hier vind je informatie over een klein stukje dat we zullen 3D-printen voor het stoeltje te verhogen op aanvraag van Lieve.

## Voorstel gekregen door Ergo
We hebben een voorstel gekregen voor de stoel hoger te doen kantelen zodat het kindje veilig in de auto kan zitten.
Ergo zei voor een stukje te 3D-printen en dan zo een groot genoeg stukje te hebben.

## Schets voor stukje
We maakten een schets voor het stukje met gekregen afmetingen.
- hoogte = 6cm
- lengte = 10cm

Voor dit visueel voor te stellen zal ik een foto van mijn schets tonenen ook nog een 3D beeld.

schets van verhoogstuk
Visueel beeld van verhoogstuk (3D)

Eindresultaat van het verhoogstuk:

visueel beeld van het stuk
visueel beeld van het stuk

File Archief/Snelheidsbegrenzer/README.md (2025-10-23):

# Snelheidsbegrenzing
Dit is een bestand over de onderdelen die we onderzocht hebben om de snelheid te begrenzen, 
maar we hebben geen snelheidsbegrenzer meer nodig aangezien we de low speed modus zullen gebruiken.

## Snelheidsbegrenzer

### Mogelijke opties

#### DC 10-50V PWM motor controller met schakelaar

Dit is een motor controller met een veelzijdige schakelaar met een ingangsspanning van 12V, 24V, 36V of 48V, ontworpen voor het regelen van de snelheid en richting van gelijkstroommotoren. Met behulp van Pulse Width Modulation (PWM) kan de regelaar de motorsnelheid nauwkeurig aanpassen. Dit zorgt ervoor om de rotatiesnelheid van de motor te veranderen en aan te passen. Ook is er een schakelaar om de motor in of uit te schakelen.

- Een ingangsspanning van 10V DC tot 55V DC
- De uitgangsspanning is lineair met de belasting
- De maximum stroom is 40A
- Er is vooruit & achteruit ondersteuning
- Het is regelbaar via een 100K potentiometer
- Een bestuuringsfrequentie van 15 Khz

---
#### DC motor snelheidsregelaar 9-60V

Deze motor maakt het mogelijk gelijkstroommotoren te bedienen. Met de vooruit/achteruit schakelaar verander je eenvoudig de draairichting en met de potmeter regel je de snelheid. Met behulp van Pulse Width Modulation (PWM) kan de regelaar de motorsnelheid nauwkeurig aanpassen. Dit zorgt ervoor om de rotatiesnelheid van de motor te veranderen en aan te passen.

- Bedrijfsspanning: DC9V-60V
- Lineaire uitgangsspanning onder belasting
- Aanhoudende stroom: 18A
- Snelheidspotentiometer
- Er is vooruit & achteruit ondersteuning

---

#### SmartDrive DC motor driver

Deze motor maakt het mogelijk gelijkstroommotoren te bedienen. De motor kan 60A per kanaal voeden. 
Het kan ook bestuurd worden via een joystick of via een microcontroller.

- Ingansspanning: DC7V-45V
- 2 kanalen om 2 motoren aan te sturen
- Aanhoudende stroom: 60A, max 100A
- 16Khz schakelfrequentie
- Er is vooruit & achteruit ondersteuning
---

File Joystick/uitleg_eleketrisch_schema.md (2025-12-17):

# Uitleg Elektrisch schema

## Joystick
Alle blauwe kabels zijn datakabels die je op de volgende pinnen soldeert:

- pin 21 voor vooruit
- pin 25 voor achteruit
- pin 17 voor links
- pin 22 voor rechts

Het maakt niet uit hoe je de joystick positioneert, zolang je logica maar overeenkomt met de gewenste richtingen.
Alle zwarte kabels gaan naar de GND van je ESP.

## H-brug
De rode kabels zijn de voedingen. Je kunt zien dat er twee afzonderlijke voedingen zijn: de voeding van de ESP (5V), die je gebruikt om de H-brug van stroom te voorzien, en de voeding van de auto. Deze laatste sluit je aan op de dc converter die je aansluit op de voeding van de auto(24V)

Daarnaast zie je nog twee groene kabels. Deze dienen om de H-brug aan te sturen zodat deze kan schakelen tussen links- en rechtsom draaien:

- pin 27 voor DN1
- pin 26 voor DN2
## Auto 
Bij de auto zie je dat je twee kabels moet aansluiten. Dit komt doordat je de originele vooruit/achteruit-joystick vervangt door je eigen joystick. Je sluit het als volgt aan:

- pin 2 op de gele kabel in de auto
- pin 15 op de groene kabel

Daarnaast blijft er nog een zwarte kabel over in de auto; deze sluit je gewoon aan op de GND van je ESP.

## Esp

Om de ESP te voeden hebben we een DC-converter met USB-aansluiting aangeschaft, zodat we de ESP rechtstreeks kunnen aansluiten. Deze converter zou normaal tot 24 V moeten werken, maar tijdens onze tests viel hij al uit bij 22 V. Daarom hebben we een extra DC-converter van 24 V naar 12 V gekocht, die we bovendien gebruiken om de motor van stroom te voorzien.

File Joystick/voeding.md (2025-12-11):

# Voeding

## Motor 
Om de motor van stroom te voorzien, wilden we oorspronkelijk rechtstreeks aftakken van de voeding van de auto. Hiervoor moesten we twee kabels doorknippen: de bruine en de rode kabel in de witte connector. Vervolgens soldeerden we een extra kabel aan deze verbinding. Zorg ervoor dat de kabels even dik zijn, zodat ze de benodigde stroom veilig kunnen geleiden. Breng daarna een krimpkous aan om de soldeerverbinding goed te isoleren en stevig te houden.
juiste kabels
soldering

Dit zou normaal voldoende moeten zijn om alles rechtstreeks op de H-brug aan te sluiten, maar er doken alsnog enkele problemen op die later worden toegelicht.

## esp
Om de ESP van stroom te voorzien gebruiken we een 24V-naar-5V USB-converter, zodat we rechtstreeks konden aftakken van de voeding van de auto. Tijdens het testen merkten we echter dat de converter slechts tot 22V werkte en daarna uitviel. Daarom hebben we een extra DC-DC-converter moeten aanschaffen die de spanning van 24V naar 12V omzet.

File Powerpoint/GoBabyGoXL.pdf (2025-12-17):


Project Experience 2526

1


Project Experience 2526

2


# GO BABY GO XL Project PX1



Project Experience 2526

4

# Probleemstelling


## Doel?

### Het ombouwen van een go-kart tot een

veilig en aangepast voertuig voor kinderen met een beperking.

## Hoe?

### Via een drukknop

### Via een joystick

## Wie?

Onze klant is Ergo therapie.

Project Experience 2526

5

# Voorstelling


Volledige groep | Maarten Audenaert Danaë Zutterman


Robbe Lambrechts
Maarten Audenaert
Danaë Zutterman
Mauro Carlier

Volledige groep


Robbe Lambrechts
Jarno Bostyn
Mauro Carlier


Project Experience 2526

6

# Beperkingen

# Wat beperkte ons?

- Tijd en kennis.

# Wat zijn de grootste risico’s?

- Levertijden en onverwachte gebeurtenissen.


Project Experience 2526

7

# Handleiding

# Handleiding voor de drukknop

- (https://github.com/vives-project-xp/GoBabyGoXL/tree/main/Handleidingen) Drukknop (https://github.com/vives-project-xp/GoBabyGoXL/tree/main/Handleidingen)

# Handleiding voor de joystick

- (https://github.com/vives-project-xp/GoBabyGoXL/tree/main/Handleidingen) Joystick (https://github.com/vives-project-xp/GoBabyGoXL/tree/main/Handleidingen)


Project Experience 2526

8

# Auto met drukknop


# - Aandrijving vervangen door een knop - Snelheid begrensd

# Auto met joystick


Project Experience 2526

9

# - DC-motor - Originele stang - Askoppeling


Project Experience 2526

10

# DC-motor houder

# Resultaat joystick auto


Project Experience 2526

11

# Architectuur


Project Experience 2526

12

Project Experience 2526

13

# Kostprijs Auto drukknop

Aantal | Product | Leverancier | Prijs excl BTW | Prijs incl BTW
2 | Seconden Epoxylijm | Hubo | € | 7,76 | € | 9,39
4 | Buizenklem 32mm | Hubo | € | 2,94 | € | 3,56
6 | Buizenklem 25mm | Hubo | € | 3,92 | € | 4,74
2 | Buizenklem 20mm | Hubo | € | 1,31 | € | 1,58
2 | Rubber (l=86,8cm; b=8cm) | Hubo | € | 2,82 | € | 3,41
12 | Bouten M6 20cm | Hubo | € | 8,58 | € | 10,38
12 | Zeskantdopmoer M6 | Hubo | € | 2,22 | € | 2,69
1 + 2 | Grondplaat voor stoel + zijkant platen | / | € | 8,26 | € | 10,00
1 | Verhoogstuk voor stoel + vervanging gaspedaal + vervanging HIGH SPEED LOW SPEED knop | / | € | 11,90 | € | 14,40
1 | Kill switch | / | / | /
| | Totaal | € | 49,71 | € | 60,15


Project Experience 2526

14

# Kostprijs Auto joystick


Project Experience 2526

15

# Resultaten

# Wat hebben we al bereikt?

### - Snelheidsbegrenzing - Besturing via een (joystick)/drukknop - Zijplaten & Grip van de banden

# Wat willen we nog bereiken?

### - Afstandsbediening voor de auto’s


Project Experience 2526

16

# Demo

# Einde


Project Experience 2526

17

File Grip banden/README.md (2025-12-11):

# Verbeterde Grip voor auto

## Over het project
Dit project beschrijft de oplossing voor een probleem met **gebrek aan grip** bij de achterbanden van een **elektrische auto**.
De originele achterbanden waren gemaakt van **plastic**, waardoor de auto te weinig wrijving had met de ondergrond. Dit kon leiden tot slippen, iets wat we wilden voorkomen om de veiligheid en controle te verbeteren.

---

## Doel
Het doel van dit project is om op een **eenvoudige, betaalbare en veilige manier** de **grip van de achterbanden** te verbeteren zonder het ontwerp van de auto ingrijpend te wijzigen.

---

## Oplossing
We hebben gekozen voor een praktische en duurzame oplossing door een **rubberen mat** te gebruiken als buitenlaag voor de achterbanden.

### Materialen
- **Rubbermat**: [Rubbermat op rol traanplaat – Hubo.be](https://www.hubo.be/nl/p/rubbermat-op-rol-traanplaat-1-5m-per-lopende-meter/131516/)  
- **Snijgereedschap**: Breekmes  
- **Lijm**: Pattex spraylijm  

### Werkwijze
1. De rubbermat werd op **maat gesneden** met een breekmes en een lat, zodat deze perfect rond de achterbanden past. (l=86.8cm en b=8cm) 



2. De binnenzijde van de rubbermat en de buitenzijde van de banden werden eerst **schoon gemaakt**.  
3. Vervolgens werd **Pattex spraylijm** aangebracht rondom **het plastiek** van de band.  
4. De rubbermat werd zorgvuldig om de banden gewikkeld en stevig aangedrukt via een spanband.  
5. Na het **uitharden van de lijm** was de rubberlaag stevig bevestigd.

---

## Resultaat
- Veel **meer grip** tijdens het rijden
- **Veiliger rijgedrag** voor de kinderen  
- **Eenvoudig uit te voeren** met goedkope materialen  

<p align="center">
  before
  after
</p>

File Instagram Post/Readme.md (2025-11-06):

## 1e instagram post
### Tekst:
🚗Plezier op wielen zonder zorgen 🚗

De doelstelling van dit project is om kinderen met een motorische beperking de mogelijkheid te geven zich zelfstandig voort te bewegen. Dit realiseren we met een auto waarbij het gaspedaal is vervangen door een knop op het stuur ook verbeteren we de veiligheid. De oorspronkelijke GoBabyGo auto was bedoeld voor jongere kinderen, maar nu ontwikkelen we een XL-versie voor kinderen die inmiddels te groot zijn geworden voor het vorige model.

Foto's: [Afbeeldingen](./Afbeeldingen)

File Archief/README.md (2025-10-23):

# Archief
In deze map vindt u alles wat we opgezocht hebben, maar niet uitgevoerd hebben.

## Research
- [Snelheidsbegrenzer](./Snelheidsbegrenzer) : Hier vindt u alles van research terug van de verschillende snelheidsbegrenzers die we onderzocht hebben.

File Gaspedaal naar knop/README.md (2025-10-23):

# Gaspedaal naar knop

## Doelstelling
De bedoeling hier van is dat we het gaspedaal die al op de auto zit eigenlijk gaan vervangen door een dukknop die zich op het stuur bevindt. Dit moet worden gedaan omdat de kinderen niet zo goed met hun benen kunnen bewegen waardoor we eigenlijk een drukknop nemen zodat ze zo op hun gemak zijn. 

## Oplossing 
Dit is de knop die we moeten gebruiken: 



We hebben dan de kabels van het gaspedaal er uit gehaald en deze bevestigd aan de knop.

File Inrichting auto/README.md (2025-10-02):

# Inrichting Auto - GoBabyGoXL

## Overzicht
Dit document beschrijft de inrichting en aanpassingen van de auto voor het GoBabyGoXL project. Het GoBabyGo project heeft als doel om aangepaste gocart auto's te maken voor kinderen met een beperking, zodat zij ook kunnen genieten van het rijden en spelen.

## Doelstelling
De auto wordt aangepast om kinderen met motorieke of mentale beperkingen een veilige en plezierige rijervaring te bieden. Het hoofddoel is het verhogen van de veiligheid door aangepaste zijpanelen te plaatsen die ervoor zorgen dat kinderen veilig in de auto blijven zitten. De oorspronkelijke vormgeving van de auto biedt al voldoende toegankelijkheid voor het instappen, waardoor kinderen zich comfortabel kunnen voortbewegen.

Een belangrijk aspect is de flexibiliteit van de inrichting, zodat deze aangepast kan worden aan verschillende individuele behoeften. De constructie moet robuust en duurzaam zijn om intensief gebruik aan te kunnen. Uiteindelijk heeft het project als overkoepelend doel dat elk kind, ongeacht beperking, kan genieten van het rijden en spelen met de aangepaste auto.

## Benodigde Materialen
- Basis speelgoedauto
- Aangepaste zijplaten (zie: `side_plate_gobabygo.stl`)
- Bevestigingsmateriaal

## Ontwerpbestanden
- **3D Model**: `side_plate_gobabygo.stl` - 3D printbestand voor de aangepaste zijplaat
- **Technische Tekening**: `zijkant_GoBabyGoXL.dxf` - DXF bestand voor de zijkant van de auto

## Veiligheidschecklist
- Alle bevestigingen zijn stevig vastgedraaid
- Scherpe randen zijn afgedekt
- Veiligheidsriemen functioneren correct
- Stabiliteit van de constructie is gecontroleerd

---
*Dit project is onderdeel van het GoBabyGoXL initiatief*

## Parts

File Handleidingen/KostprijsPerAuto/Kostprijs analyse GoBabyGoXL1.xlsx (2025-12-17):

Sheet: Kostprijs Drukknop
Aantal | Product | Leverancier | Prijs excl BTW | Prijs incl BTW | Link | 3D-prints | Lasercutten
2 | Seconden Epoxylijm | Hubo | €7.76 | €9.39 | https://www.hubo.be/nl/p/pattex-super-mix-universal-mini-epoxy-colle-bi-composant-6ml/249565/#specs
4 | Buizenklem 32mm | Hubo | €2.94 | €3.56 | https://www.hubo.be/nl/p/astore-buisklem-32mm-polypropyleen/890700/
6 | Buizenklem 25mm | Hubo | €3.92 | €4.74 | https://www.hubo.be/nl/p/buisklem-pp-25mm/972187/
2 | Buizenklem 20mm | Hubo | €1.31 | €1.58 | https://www.hubo.be/nl/p/scala-buisklem-20mm-polypropyleen/994224/
2 | Rubber (l=86,8cm; b=8cm) | Hubo | €2.82 | €3.41 | https://www.hubo.be/nl/p/rubbermat-op-rol-traanplaat-1-5m-per-lopende-meter/131516/
12 | Bouten M6 20cm | Hubo | €8.58 | €10.38 | https://www.hubo.be/nl/p/mack-binnenzeskantbout-m6-20mm-verzinkt-7-stuks/208802/
12 | Zeskantdopmoer M6 | Hubo | €2.22 | €2.69 | https://www.hubo.be/nl/p/pgb-fasteners-zeskantdopmoer-din1587-m6-zwart-12-stuks/1057451/
1 + 2 | Grondplaat voor stoel + zijkant platen | / | €8.26 | €10.00 | https://github.com/vives-project-xp/GoBabyGoXL/tree/main/Lasercutten |  | x
1 | Verhoogstuk voor stoel + vervanging gaspedaal + vervanging HIGH SPEED LOW SPEED knop | / | €11.90 | €14.40 | https://github.com/vives-project-xp/GoBabyGoXL/tree/main/3d-prints | x
1 | Kill switch | / | / | / | /
 |  | Totaal | €49.71 | €60.15

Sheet: Kostprijs joystick
Aantal | Product | Leveranciers | Prijs exl BTW | Prijs incl BTW | Link | 3D print | Lasercutter | Kolom9 | Kolom10 | Kolom11
1 | Joystick | Conrad | 7.84 € | €9.49 | https://www.conrad.be/nl/p/joy-it-arcade-joystick-professional-8-invoerapparaat-geschikt-voor-arduino-banana-pi-cubieboard-pcduino-raspberry-pi-1555268.html?c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
1 | DC Motor | TinyTronics | 26.45 € | €32.00 | https://www.tinytronics.nl/nl/mechanica-en-actuatoren/motoren/dc-motoren/aslong-pg42-775-transmissiemotor-24v-dc-90rpm
1 | Esp32 | TinyTronics | 10.74 € | €13.00 | https://www.tinytronics.nl/nl/development-boards/microcontroller-boards/met-wi-fi/lilygo-ttgo-t-display-v1.1-esp32-met-1.14-inch-tft-display
1 | 24V module | Amazon.nl | 3.72 € | €4.50 | https://www.amazon.nl/gp/product/B07JLTTZXL?smid=A3U3NV7MT8POQS&psc=1
1 | H-brug | Otronic | 2.15 € | €2.60 | https://www.otronic.nl/nl/l298n-motor-driver-board-rood.html?source=googlebase
2 | Seconden Epoxylijm | Hubo | 7.76 € | €9.39 | https://www.hubo.be/nl/p/pattex-super-mix-universal-mini-epoxy-colle-bi-composant-6ml/249565/#specs
4 | Buizenklem 32mm | Hubo | 2.94 € | €3.56 | https://www.hubo.be/nl/p/astore-buisklem-32mm-polypropyleen/890700/
6 | Buizenklem 25mm | Hubo | 3.92 € | €4.74 | https://www.hubo.be/nl/p/buisklem-pp-25mm/972187/
2 | Buizenklem 20mm | Hubo | 1.31 € | €1.58 | https://www.hubo.be/nl/p/scala-buisklem-20mm-polypropyleen/994224/
2 | Rubber (l=86,8cm; b=8cm) | Hubo | 2.82 € | €3.41 | https://www.hubo.be/nl/p/rubbermat-op-rol-traanplaat-1-5m-per-lopende-meter/131516/
12 | Bouten M6 20cm | Hubo | 8.58 € | €10.38 | https://www.hubo.be/nl/p/mack-binnenzeskantbout-m6-20mm-verzinkt-7-stuks/208802/
12 | Zeskantdopmoer M6 | Hubo | 2.22 € | €2.69 | https://www.hubo.be/nl/p/pgb-fasteners-zeskantdopmoer-din1587-m6-zwart-12-stuks/1057451/
1 + 2 | Grondplaat voor stoel + zijkant platen | / | 8.26 € | €10.00 | https://github.com/vives-project-xp/GoBabyGoXL/tree/main/Lasercutten |  | x
1 | 3D prints (gaspedaal,knop,knop2,houder,stoel) | / | 11.90 € | €14.40 | https://github.com/vives-project-xp/GoBabyGoXL/tree/main/3d-prints | x
1 | Assen koppeling | Motedis | 4.12 € | €4.98 | www.motedis.be/nl/Assen-Koppelingen-flexibel-Mot-D25L30-8-12mm
1 | Kill switch | / | / | /
1 | 24v naar 12v | Hubo | 20.66 € | €25.00 | https://www.ebay.com/itm/404296383563
 |  | Totaal | 125.39 € | €151.72

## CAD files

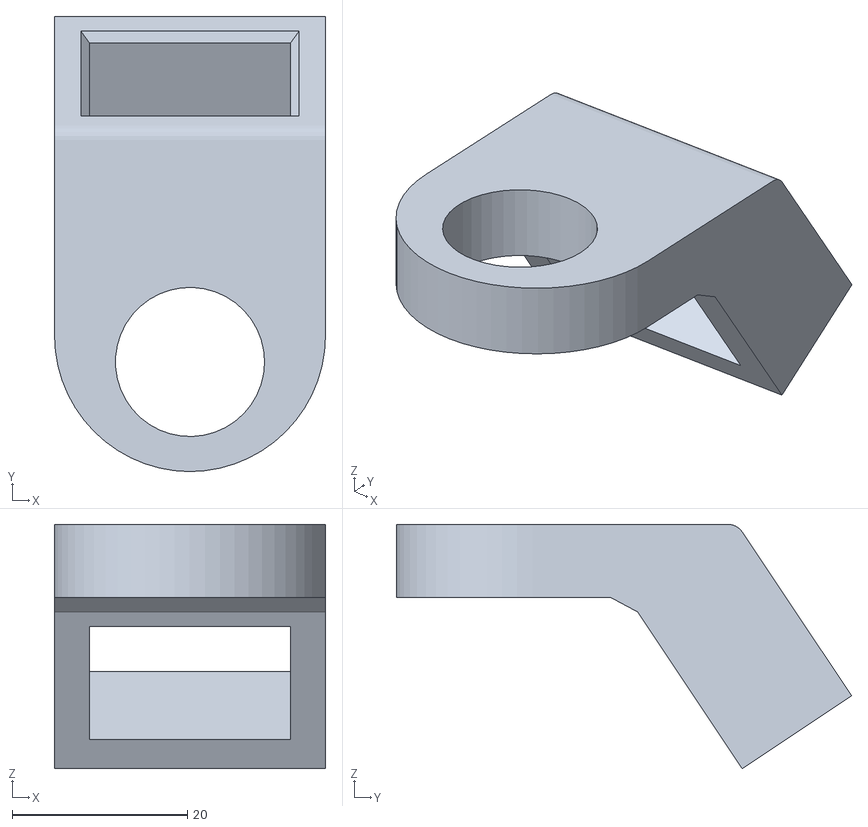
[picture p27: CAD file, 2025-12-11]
3d-prints/DC-voeding houder/servo_houder_tilted_extra.stl
30.9 x 51.9 x 27.9

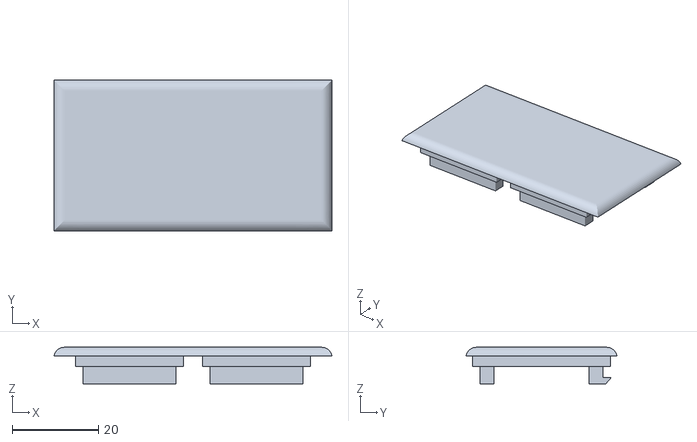
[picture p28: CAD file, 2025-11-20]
3d-prints/Dekseltje voor knop en hendel/deksel_combo.stl
64.5 x 35.0 x 8.50

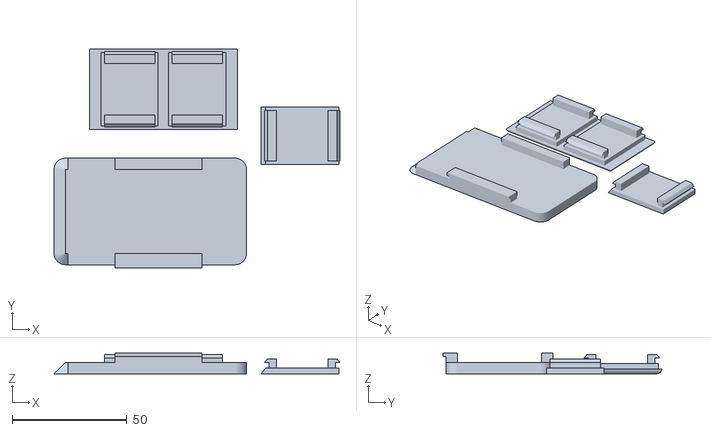
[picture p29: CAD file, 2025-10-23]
3d-prints/Gaspedaal plaatje/combie_deksel_&_gaspedaal.stl
124.8 x 95.5 x 9.00

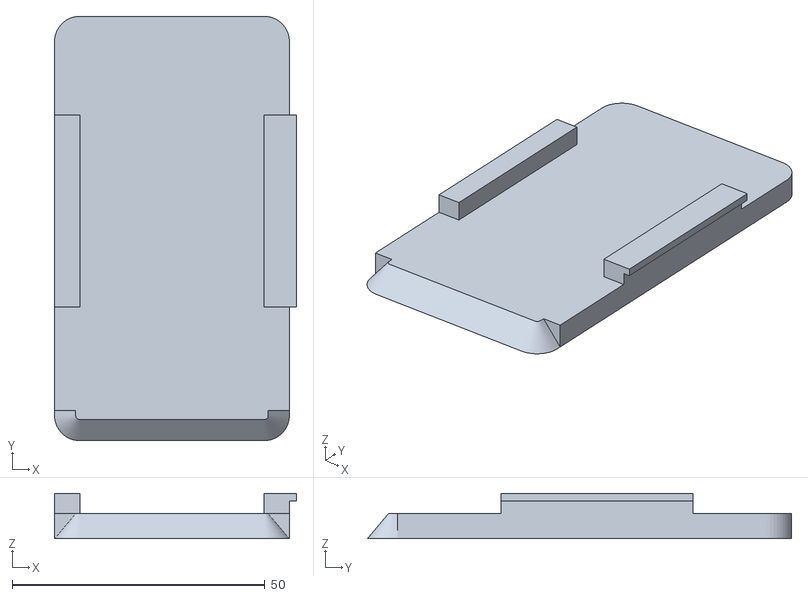
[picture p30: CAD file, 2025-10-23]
3d-prints/Gaspedaalv2.stl
47.9 x 84.0 x 9.00

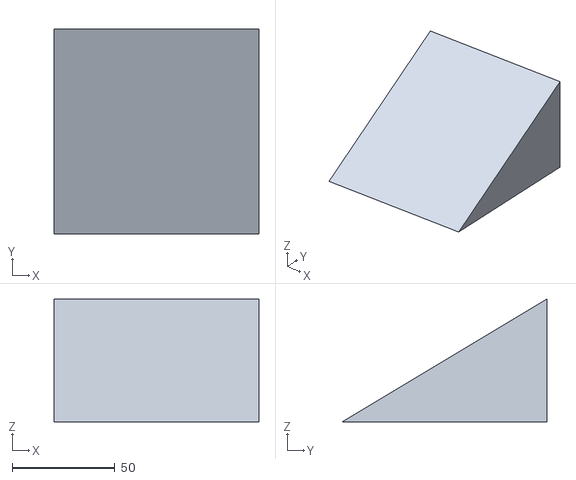
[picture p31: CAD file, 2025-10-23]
3d-prints/Helling stoeltje/HellingPX1 v2.stl
100.0 x 100.0 x 60.0

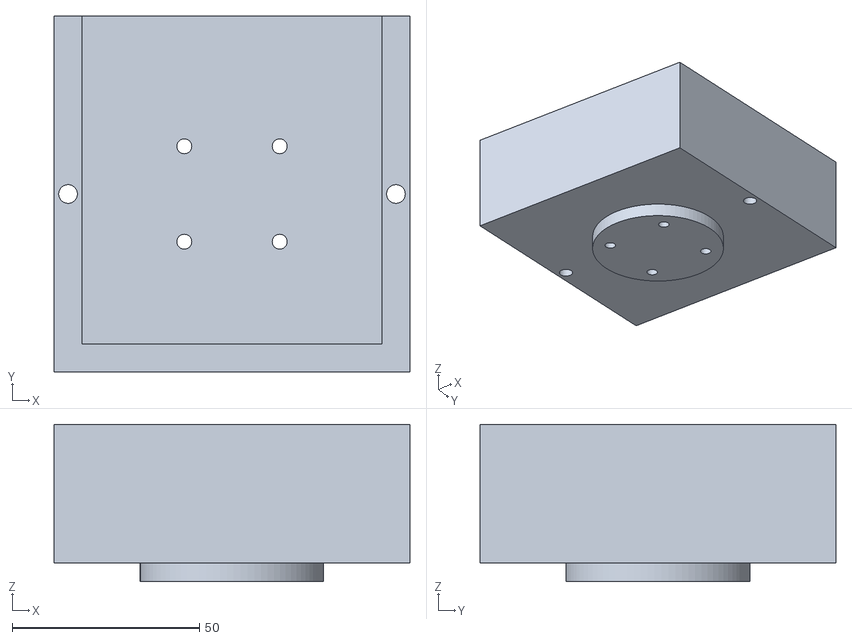
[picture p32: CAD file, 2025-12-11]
3d-prints/Joystick behuizing/box joystick.stl
95.0 x 95.0 x 42.0

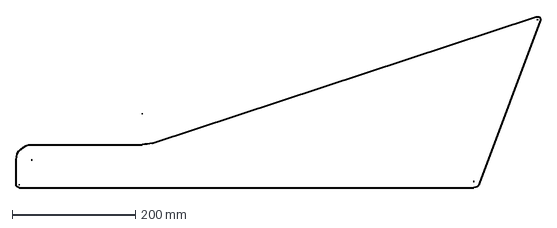
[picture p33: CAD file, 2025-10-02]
Inrichting auto/bestanden/zijkant_GoBabyGoXL.dxf
852.0 x 278.4 mm

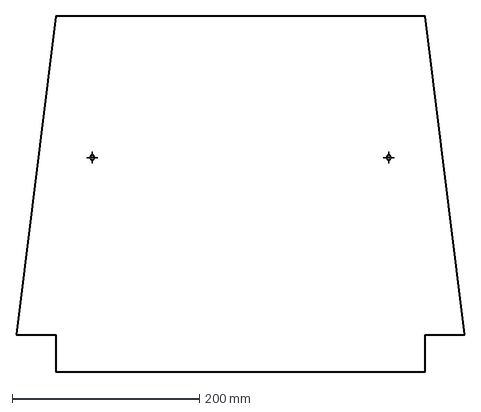
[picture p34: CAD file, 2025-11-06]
Lasercutten/Grondplaat/Grondplaat_v3.dxf
480.0 x 380.0 mm

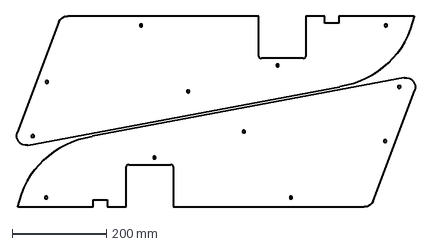
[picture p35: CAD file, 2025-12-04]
Lasercutten/Zijkant platen/side plate go baby go.dxf
849.5 x 405.5 mm

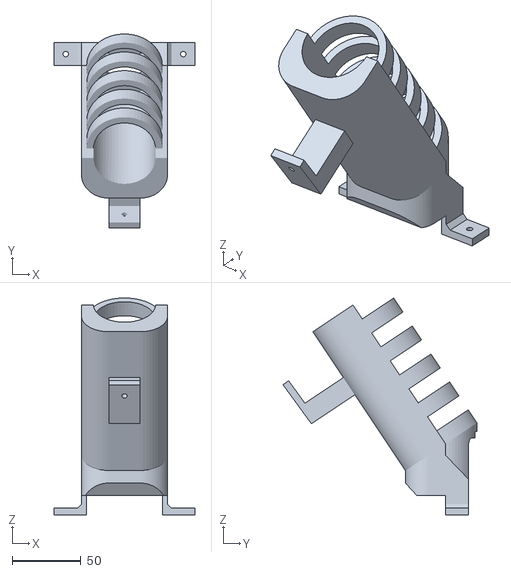
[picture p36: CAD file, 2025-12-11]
3d-prints/DC-voeding houder/servo_houder_tilted.stl
102.4 x 140.9 x 157.7

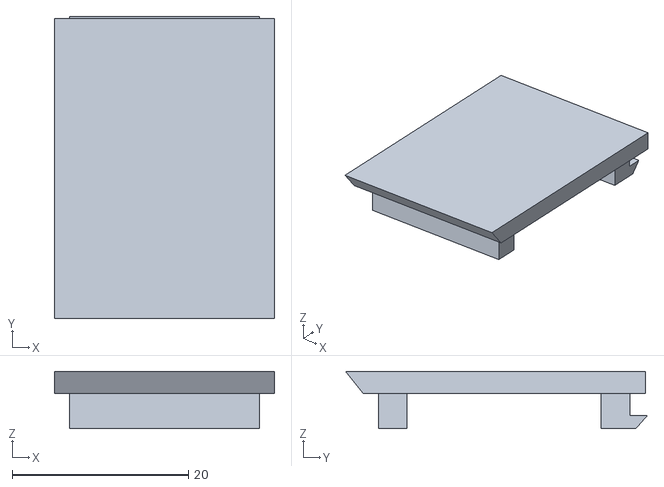
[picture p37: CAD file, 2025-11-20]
3d-prints/Dekseltje voor knop en hendel/dekseltje_sloped.stl
25.0 x 34.2 x 6.50

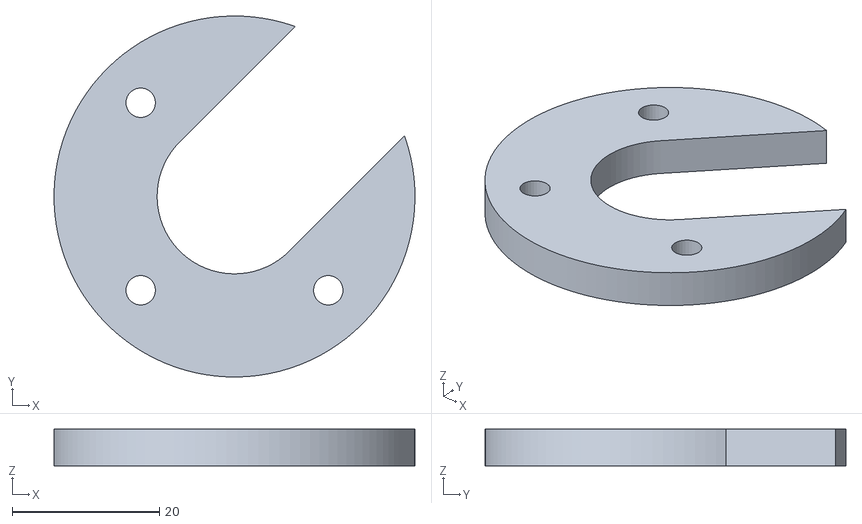
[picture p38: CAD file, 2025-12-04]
3d-prints/Joystick behuizing/montage joy2.stl
49.0 x 49.0 x 5.00

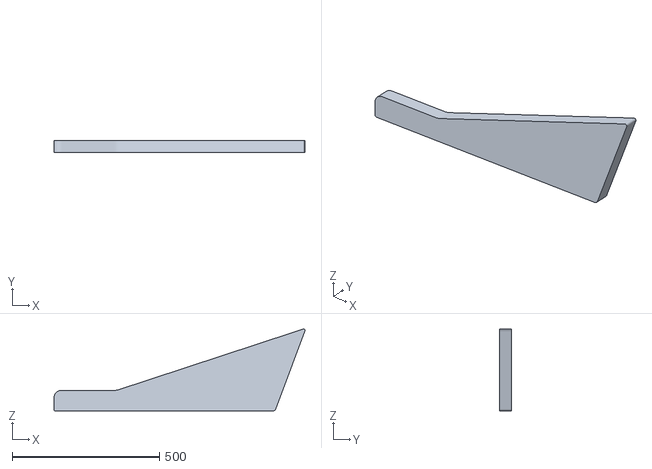
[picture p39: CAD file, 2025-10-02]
Inrichting auto/bestanden/side_plate_gobabygo.stl
851.6 x 40.0 x 278.0

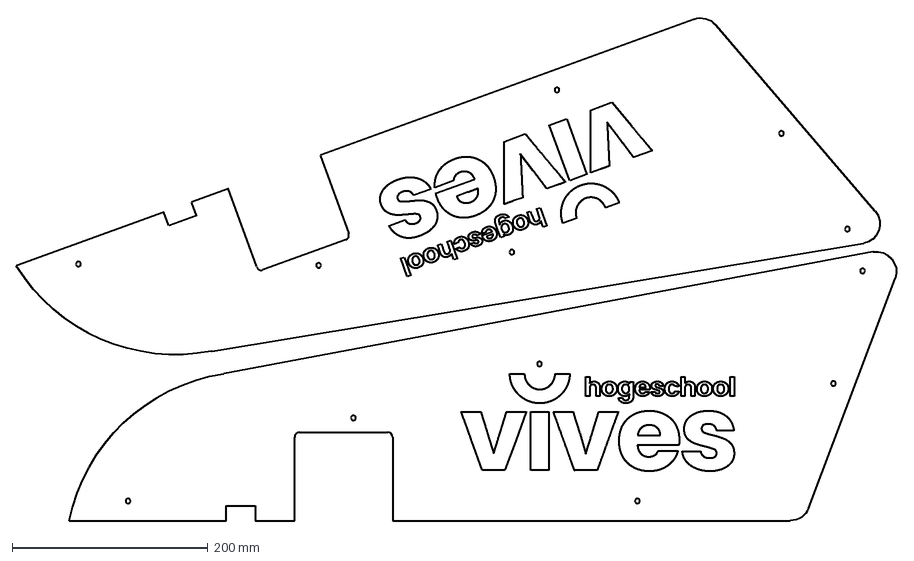
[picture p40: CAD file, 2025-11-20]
Lasercutten/Zijkant platen/sideplates_with_logo.dxf
899.5 x 514.8 mm

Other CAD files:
3d-prints/Gaspedaal plaatje/Gaspedaalv2.stl
3d-prints/Dekseltje voor knop en hendel/deksel_combo v2.stl
3d-prints/Gaspedaal plaatje/Gaspedaalv3.stl
3d-prints/Joystick behuizing/bovenkant.stl
3d-prints/Dekseltje voor knop en hendel/deksel_combo v1.stl
3d-prints/Dekseltje voor knop en hendel/dekseltje_sloped v2.stl
3d-prints/Gaspedaal plaatje/Gaspedaal.stl
Lasercutten/Zijkant platen/SidePlatesWithLogo.dxf

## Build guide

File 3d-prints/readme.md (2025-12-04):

# 3D-PRINTS
Deze map bevat 3D-print onderdelen voor verschillende stukjes te 3D-printen zoals het plaatje voor het gaspedaal, helling voor de stoel beter te bevestigen, een dekseltje voor de knop en hendel, de houder voor de DC-Motor en de behuizing van de joystick

## Onderdelen
- [Gaspedaal plaatje](./Gaspedaal%20plaatje) : Hier vindt u alle stl-files om het plaatje van het gaspedaal te 3D-printen.
- [Helling stoeltje](./Helling%20stoeltje) : Hier vindt u de stl-file om de helling van het stoeltje te 3D-printen.
- [Dekseltje voor knop en hendel](./Dekseltje%20voor%20knop%20en%20hendel) : Hier vindt u alle stl-files om het dekseltje voor knop en hendel te 3D-printen.
- [DC-Motor houder](./DC-voeding%20houder) : Hier vindt u de stl-file om de houder van de DC-Motor te 3D-printen.
- [Behuizing Joystick](./Joystick%20behuizing): Hier vindt u de stl-file om de behuizing van de joystick te 3D-printen.

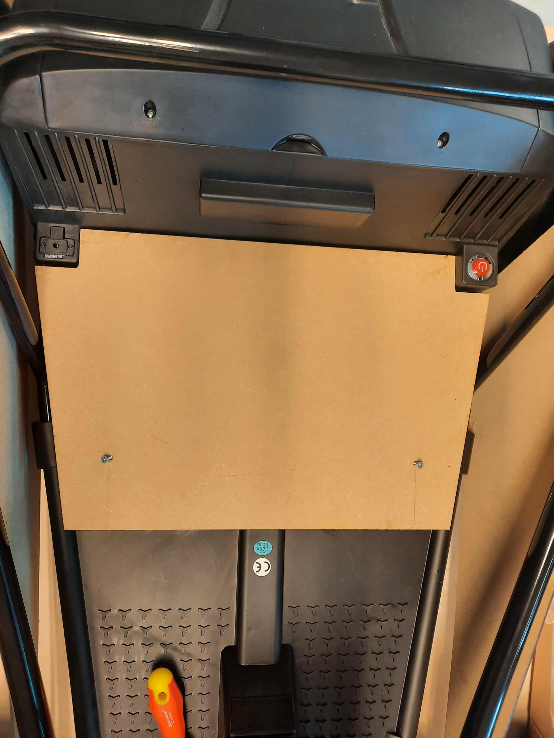
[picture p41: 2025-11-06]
Handleidingen/afbeeldingen/grontplaarMontage.jpg

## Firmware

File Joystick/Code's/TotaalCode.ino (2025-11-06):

// joystick inputs
#define drukvooruit 25
#define drukachteruit 21
#define druklinks 22
#define drukrechts 17

// vooruit achteruit auto
const int switchPin1 = 2;   // uitgang voor stand 1
const int switchPin2 = 15;   // uitgang voor stand 2

// sturing 
const int IN1A = 27;  // Richting pin 1
const int IN2A = 26;  // Richting pin 2
 
boolean vooruitStatus =  true;
boolean achteruitStatus =  true;
boolean linksStatus = true;
boolean rechtsStatus =  true;
 
 
void setup() {
  pinMode(drukvooruit, INPUT_PULLUP);
  pinMode(drukachteruit, INPUT_PULLUP);
  pinMode(druklinks, INPUT_PULLUP);
  pinMode(drukrechts, INPUT_PULLUP);

  pinMode(switchPin1, OUTPUT);
  pinMode(switchPin2, OUTPUT);

  // Begin met alles uit
  digitalWrite(switchPin1, HIGH);
  digitalWrite(switchPin2, HIGH);

  pinMode(IN1A, OUTPUT);
  pinMode(IN2A, OUTPUT);

  Serial.begin(9600);
}
 
void loop() {
  vooruitStatus = digitalRead(drukvooruit);
  achteruitStatus = digitalRead(drukachteruit);
  linksStatus = digitalRead(druklinks);
  rechtsStatus = digitalRead(drukrechts);

  // Middelste stand (geen verbinding)
  digitalWrite(switchPin1, HIGH);
  digitalWrite(switchPin2, HIGH);
  Serial.println("Middelste stand (geen verbinding)");

  if (vooruitStatus == false) {
    digitalWrite(switchPin1, LOW);   
    digitalWrite(switchPin2, HIGH);
    Serial.println("Stand 1 actief (vooruit)");
  }

  if (achteruitStatus == false) {
    digitalWrite(switchPin1, HIGH);
    digitalWrite(switchPin2, LOW);
    Serial.println("Stand 2 actief (achteruit)");
  }

  if (linksStatus == false) {
    Serial.println("links");
    digitalWrite(IN1A, HIGH);
    digitalWrite(IN2A, LOW);
  } 
  else if (rechtsStatus == false) {
    Serial.println("rechts");
    digitalWrite(IN1A, LOW);
    digitalWrite(IN2A, HIGH);
  } 
  else {
    // Alleen uitzetten als er geen richting actief is
    digitalWrite(IN1A, LOW);
    digitalWrite(IN2A, LOW);
  }

  delay(200);  
}

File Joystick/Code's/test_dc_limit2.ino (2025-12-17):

// joystick inputs (active LOW)
#define drukvooruit 25
#define drukachteruit 21
#define druklinks 22
#define drukrechts 17

// vooruit achteruit auto
const int switchPin1 = 2;
const int switchPin2 = 15;

// sturing motor (H-brug)
const int IN1A = 27;
const int IN2A = 26;

// basis tijdlimiet (centrum)
const unsigned long basisLimiet = 6000; // 2s

// maximale extra tijd als we aan een kant zitten
const unsigned long extraLimiet = 4000; // 4s, totaal dus max. 6s

// positie variabele (-100 = links, 0 = midden, 100 = rechts)
int stuurPositie = 0;

// timers & blokkades
unsigned long startTijdLinks = 0;
unsigned long startTijdRechts = 0;
bool blockedLeft = false;
bool blockedRight = false;

void setup() {
  pinMode(drukvooruit, INPUT_PULLUP);
  pinMode(drukachteruit, INPUT_PULLUP);
  pinMode(druklinks, INPUT_PULLUP);
  pinMode(drukrechts, INPUT_PULLUP);

  pinMode(switchPin1, OUTPUT);
  pinMode(switchPin2, OUTPUT);

  pinMode(IN1A, OUTPUT);
  pinMode(IN2A, OUTPUT);

  Serial.begin(9600);
}

unsigned long berekenLimiet() {
  // absolute afstand tot midden
  int afstand = abs(stuurPositie); // 0–100

  // hoe dichter bij uiterste stand, hoe meer limiet
  float factor = afstand / 100.0; // 0.0 – 1.0

  return basisLimiet + (extraLimiet * factor);
}

void loop() {
  bool vooruit = (digitalRead(drukvooruit) == LOW);
  bool achteruit = (digitalRead(drukachteruit) == LOW);
  bool links = (digitalRead(druklinks) == LOW);
  bool rechts = (digitalRead(drukrechts) == LOW);

  unsigned long now = millis();

  // ---- Vooruit/achteruit zoals eerder ----
  digitalWrite(switchPin1, HIGH);
  digitalWrite(switchPin2, HIGH);

  if (vooruit) {
    digitalWrite(switchPin1, LOW);
    digitalWrite(switchPin2, HIGH);
  }

  if (achteruit) {
    digitalWrite(switchPin1, HIGH);
    digitalWrite(switchPin2, LOW);
  }

  // ---- Dynamische tijdlimiet ----
  unsigned long huidigeLimiet = berekenLimiet();

  // --- LINKS ---
  if (links) {
    if (startTijdLinks == 0) startTijdLinks = now;

    if (!blockedLeft && (now - startTijdLinks < huidigeLimiet)) {
      digitalWrite(IN1A, HIGH);
      digitalWrite(IN2A, LOW);
      if (stuurPositie > -100) stuurPositie--;   // links = negatief
    }
    else {
      blockedLeft = true;
      digitalWrite(IN1A, LOW);
      digitalWrite(IN2A, LOW);
      Serial.println("LIMIT LINKS bereikt");
    }
  }
  else {
    startTijdLinks = 0;
    blockedLeft = false;
  }

  // --- RECHTS ---
  if (rechts) {
    if (startTijdRechts == 0) startTijdRechts = now;

    if (!blockedRight && (now - startTijdRechts < huidigeLimiet)) {
      digitalWrite(IN1A, LOW);
      digitalWrite(IN2A, HIGH);
      if (stuurPositie < 100) stuurPositie++;   // rechts = positief
    }
    else {
      blockedRight = true;
      digitalWrite(IN1A, LOW);
      digitalWrite(IN2A, LOW);
      Serial.println("LIMIT RECHTS bereikt");
    }
  }
  else {
    startTijdRechts = 0;
    blockedRight = false;
  }

  // Extra veiligheid
  if (!links && !rechts) {
    digitalWrite(IN1A, LOW);
    digitalWrite(IN2A, LOW);
  }

  // debug
  Serial.print("Positie: ");
  Serial.print(stuurPositie);
  Serial.print("    Limiet: ");
  Serial.println(huidigeLimiet);

  delay(10);
}

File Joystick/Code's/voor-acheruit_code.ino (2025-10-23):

// Schakelaar testprogramma

const int switchPin1 = 22;   // eerste stand
const int switchPin2 = 21;   // tweede stand

void setup() {
  Serial.begin(9600);
  
  pinMode(switchPin1, INPUT_PULLUP);
  pinMode(switchPin2, INPUT_PULLUP);

  Serial.println("Schakelaar test gestart!");
  Serial.println("Zet de schakelaar in verschillende standen...");
}

void loop() {
  int state1 = digitalRead(switchPin1);
  int state2 = digitalRead(switchPin2);

  if (state1 == LOW && state2 == HIGH) {
    Serial.println("Stand 1 actief vooruit");
  } else if (state2 == LOW && state1 == HIGH) {
    Serial.println("Stand 2 actief achteruit");
  } else if (state1 == HIGH && state2 == HIGH) {
    Serial.println("neutraal (middelste stand)");
  } else {
    Serial.println("Beide pinnen laag neutraal");
  }

  delay(500);
}

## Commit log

2025-10-02 Add image to DC 10-50V PWM motor controller section
    Added image reference for DC 10-50V PWM motor controller.
2025-10-02 Update image height in README.md
    Adjusted image size in README for motor controller.
2025-10-02 Fix typo in README.md output voltage description
2025-10-02 Expand README with speed limiting component details
    Added detailed information about speed limiting components and options for motor control.
2025-10-02 Update README.md
    Removed detailed descriptions of various motor controllers and their specifications from the README.
2025-10-02 Update README.md
    Updated image reference for SmartDrive DC motor driver in README.
2025-10-02 readme ingevuld en bestanden bij gestoken
    [side_plate_gobabygo.stl, zijkant_GoBabyGoXL.dxf]
2025-10-16 zijplaat veranderingen
    [side_plate_go_baby_go.dxf, side_plate_go_baby_go.stl, side_plate_gobabygo.stl, zijkant_GoBabyGoXL.dxf]
2025-10-16 Create deksel_combo v1.stl
    [deksel_combo v1.stl]
2025-10-22 update servo_houder
2025-10-23 3d print helling
    [HellingPX1 v1.stl]
2025-10-23 aanpassingen voor helling
    [HellingPX1 v1.stl, HellingPX1 v2.stl]
2025-10-23 Update
    Added a section listing 3D print components.
2025-10-23 Update README.md
    Added instructions for securing the soldered connection.
2025-10-23 servo 3d print
    [servo_houder2 v2.stl]
2025-10-23 Enhance soldering instructions for purple wire
    Added instructions for securing the purple wire during soldering.
2025-11-06 servo update fotos
2025-11-06 servo foto
2025-11-06 grondplaat dxf
    [grondplaat2.dxf]
2025-11-06 Correct link case in Readme.md
2025-11-06 MDF zijplaten
    [SidePlatesWithLogo.dxf, side plate go baby go Drawing v5 Sheet1.dxf]
2025-11-06 grondplaat fotos resultaat
    [Grondplaat_v3.dxf]
2025-11-06 dc voeding houder
    [servo_houder2 v2.stl]
2025-11-06 Update Readme.md
    Updated images and specifications for two DC-Motors.
2025-11-20 Create side plate go baby go Drawing v6.dxf
    [side plate go baby go Drawing v6.dxf]
2025-11-20 DXF FILES
    [side plate go baby go Drawing v5 Sheet1.dxf, side plate go baby go.dxf, sideplates_with_logo.dxf]
2025-11-20 Fix image source for soldered connection
    Updated image reference in the readme file.
2025-11-20 Update readme with installation and assembly sections
2025-11-20 new stl
    [deksel_combo.stl, dekseltje_sloped.stl]
2025-12-04 correcte lasercut
    [servo_houder_tilted.stl, side plate go baby go.dxf]
2025-12-04 update
    Updated project title to indicate it's a prototype.
2025-12-04 Stuurmechanisme met DC-Motor
2025-12-04 foto dc-motor print
2025-12-04 Update print statement from 'Hello' to 'Goodbye'
2025-12-11 Update print statement to say 'Goodbye World'
2025-12-11 servo houder
    [servo_houder2 v2.stl, servo_houder_tilted.stl, servo_houder_tilted_extra.stl]
2025-12-11 Update print statement to show 'Goodbye World'
